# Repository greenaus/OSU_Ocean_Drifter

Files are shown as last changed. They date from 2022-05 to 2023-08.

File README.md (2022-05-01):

# OSU_Ocean_Drifter
The code repo for the HC 407 ocean drifter dev-kit

## ArudinoGPS.ino Dependencies:

Adafruit Unified Sensor  
Adafruit Circuit Playground  
Adafruit MAX31856 Library  
DHT sensor library  
Tiny GPS

## Current Arduino Pinout
### DHT Humidity Sensor:
plus  -> 5V

out   -> D2

minus -> GND

### GPS
VCC -> 5V  (Needs external source. Arudino can't provide enough power to run!)

RX  -> D3

TX  -> D4

GND -> GND

### Max31856 Thermocouple:
Vin -> 5V

GND -> GND

SCK -> D13

SDO -> D12

SDI -> D11

CS  -> D10

### SD Card (Tentative):
CS   -> D9

SCK  -> D13

MOSI -> D11

MISO -> D12

VCC  -> 5V

GND  -> GND

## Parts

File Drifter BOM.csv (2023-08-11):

Components | Description | Unit Price | Quantity | Address
LM3940IT-3.3/NOPB-ND | 3.3 V Regulator |  | 1
MAX6675ISA+TCT-ND | Thermocouple |  | 2
74VHC125MTCXCT-ND | Non-inv buffer |  | 1
490-GRM02YR60J104ME01LCT-ND | 0.1uF Cap |  | 3
490-10410-1-ND | 0.47uF Cap |  | 1
1276-2420-1-ND | 47uF Cap |  | 1
WM6357CT-ND | SD Card holder |  | 1
118-CR0805-FX-1300ELFCT-ND | 130 Ohm |  | 5
475-1410-1-ND | Green LED |  | 5
GY-NEO6MV2 NEO-6m | GPS |  | 1 | Amazon.com: HiLetgo GY-NEO6MV2 NEO-6M GPS Flight Controller Module 3V-5V with Super Strong Ceramic Antenna for Arduino EEPROM APM 2.5 : Electronics
LM2956 | Battery voltage regulator |  | 1
 | 2pin 2.54mm pitch screw terminal |  | 1 | https://www.amazon.com/Screw-Terminal-Connector-2-54mm-Universal/dp/B07QLXR1V9

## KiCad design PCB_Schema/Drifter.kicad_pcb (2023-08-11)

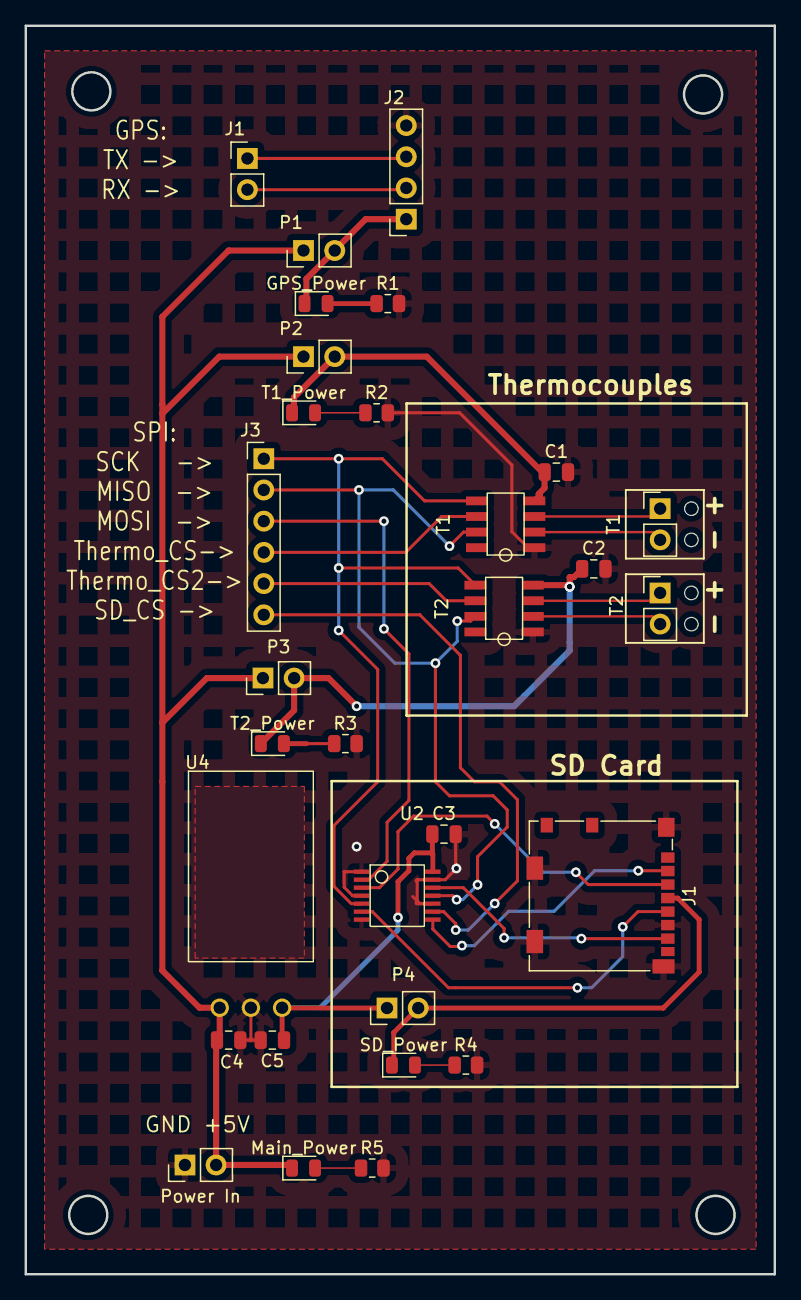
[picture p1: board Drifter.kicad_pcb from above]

Board: 2 copper layers, 61.0 x 101.6 mm, 30 parts (0 on the bottom side), 19 nets.

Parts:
C1, C2, C3, C4, C5: C_0805_2012Metric
GPS_Power: LED_0805_2012Metric
J1: microSD_HC_Molex_104031-0811
J1#2: PinHeader_1x02_P2.54mm_Vertical
J2: PinSocket_1x04_P2.54mm_Vertical
J3: PinHeader_1x06_P2.54mm_Vertical
Main_Power: LED_0805_2012Metric
P1, P2, P3, P4: PinHeader_1x02_P2.54mm_Vertical
Power In: PinHeader_1x02_P2.54mm_Vertical
R1, R2, R3, R4, R5: R_0805_2012Metric
SD_Power: LED_0805_2012Metric
T1, T2#2: PinHeader_1x02_P2.54mm_Vertical
T1#2, T2: Max6675
T1_Power, T2_Power: LED_0805_2012Metric
U2: 74VHC125
U4: LM3940

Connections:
+3.3V: C3.1, C5.1, J1.4, P4.1, P4.2, SD_Power.1, U2.14, U4.3
+5V: C1.1, C2.1, C4.1, GPS_Power.1, J2.1, Main_Power.1, P1.1, P1.2, P2.1, P2.2, P3.1, P3.2, Power In.2, T1#2.4, T1_Power.1, T2.4, T2_Power.1, U4.1
/CS_SD: J3.6, U2.9
/CS_Thermo: J3.4, T1#2.6
/MISO: J3.2, T1#2.7, T2.7, U2.11
/MOSI: J3.3, U2.2
/SCK: J3.1, T1#2.5, T2.5, U2.5
CD: J1.2, U2.8
CLK: J1.5, U2.6
CMD: J1.3, U2.3
CS_Thermo2: J3.5, T2.6
DAT0: J1.7, U2.12
GND: C1.2, C2.2, C3.2, C4.2, C5.2, J1.6, J1.11, J2.4, Power In.1, R1.2, R2.2, R3.2, R4.2, R5.2, T1#2.1, T2.1, U2.1, U2.4, U2.7, U2.10, U2.13, U4.2
RX: J1#2.2, J2.2
T2+: T2.3, T2#2.1
T2-: T2.2, T2#2.2
T+: T1.1, T1#2.3
T-: T1.2, T1#2.2
TX: J1#2.1, J2.3

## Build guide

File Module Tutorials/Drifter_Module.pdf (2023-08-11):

## Module Overview

Introduction

The Global Position System, or GPS, is an incredibly useful tool that has seen use in a variety of industries and applications. GPS is a part of the Global Navigation Satellite System (GNSS), and is used to provide geographical location and time to receivers. It has seen a variety of uses and is one of the primary sources of navigational data and positioning. GPS is reliant on a network of satellites orbiting the earth to provide an accurate approximation of a receivers location. A receiver needs a minimum of 4 satellites in order to accurately find its location. This is accomplished by each satellite sending a continuous message to each receiver containing its identification number, location in orbit, and time of transmission. Since the signals sent by the satellites travel at the speed of light, a distance can be calculated based off time of flight, and known speed of the message.

Hardware Overview

For this course, we are using a commonly used GPS module, the GY-NEO6MV2, which sees extensive use in battery operated and small form factor applications, such as drone racing. The NEO6MV2 is a standalone GPS receiver that provides location and time information over a standard Universal Asynchronous Receiver-Transmitter (UART), connection with a micro-controller, in this case our Arduino. This UART connection is typically made with 4 direct wired connections between the module and the micro-controller. Those four connections are VCC, RX, TX, and GND.

In our application, the module slots directly into the break out board, and only two connections are required to communicate with our controller, the RX and TX pins. RX is the ”receiver” channel for the module, and TX is the ”transmitter”. The RX pin on the module will connect with the TX pin on our Arduino, and the TX pin on our module will connect with the RX pin on the Arduino. A wiring diagram is provided below as well to illustrate this point.

As for the VCC and GND pins, these are the main source of power for the module. While normally it is possible to provide power for the module directly from the controller, in this case, we are providing power for the module through the break out board. VCC is a 5V input, while GND is the common ground.

1

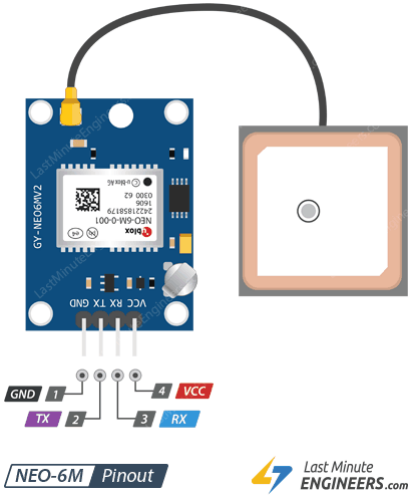
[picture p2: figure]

Figure 1: GPS Pinout

2

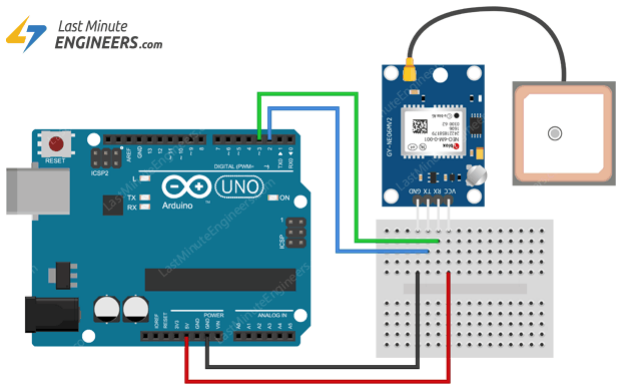
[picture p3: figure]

Figure 2: Wiring Diagram

## Module Pinout

## Wiring Guide

The figure above shows the wiring diagram used in this project. To connect the TX pin on the breakout board, to Pin 19 (RX1) on the Arduino Mega (Green Wire). RX on the breakout board, connects to Pin 18 (TX1) on the Arduino Mega (Blue Wire).

## Coding Guide

In order to use the GPS module after making these connections, we have to write some code for the Arduino to facilitate the communication. Since GPS uses a standardized communication protocol, there are numerous code libraries implemented for the Arduino to communicate with the module, and decipher the message coming from it. This module makes use of the TinyGPS++ library in the Arduino IDE. We use this library to open the serial communication ports on the Arduino, and decipher the NMEA sentences that come from the GPS unit. Below is the code you will need to get started.

Arduino

Libraries

3

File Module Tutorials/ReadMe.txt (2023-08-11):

This is the folder containing all of the tutorials for each module used in the Drifter project

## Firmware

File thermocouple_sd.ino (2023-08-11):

//libraries/files included
#include <MAX6675.h>
#include <SD.h>
#include <SPI.h>

//pin assignments
#define CS_PIN1 13
#define CS_PIN2 12
#define soPin = 50;
#define sckPin = 52;

//thermocouple initialization
MAX6675 tcouple1(CS_PIN1);
MAX6675 tcouple2(CS_PIN2);

File myFile; //file object

//data variables
int count = 0;
double temperature1 = 0;
double temperature2 = 0;
char myFileName[] = "test1.txt";
  
void setup() {
  //initialize serial
  Serial.begin(9600);

   //SD card initialization
  Serial.println("Initializing SD card...");
  if (!SD.begin(53)) {
    Serial.println("Initialization failed!");
    while(1);
  }
  Serial.println("Initialization done.");
  Serial.println();
  
 // if (SD.exists("data.txt")) SD.remove("data.txt"); //if there's already a file, delete it

//check the files name and create a new file
  for (int i = 1; i < 1000; i++) {
  char y = i+'0';
  myFileName[4] = y; // change the file name: test1.txt test2.txt.......
  
  if (SD.exists(myFileName)){ // if the file already exist
    continue;
    }
 
    Serial.println(myFileName); // Print the filename to which data is written before each run. 
    break;
  }
  
  //timer/counter1 initialization
  cli(); //stop interrupts
  TCCR1A = 0;
  TCCR1B = 0;
  TCNT1 = 0;
  OCR1A = 15624; // 1 Hz
  TCCR1B |= (1 << WGM12); //ctc mode
  TCCR1B |= (1 << CS12) | (1 << CS10); //prescaler
  TIMSK1 |= (1 << OCIE1A);
  sei(); //start interrupts
}

ISR(TIMER1_COMPA_vect) { //interrupt function to be called when timer reaches max
  count++; //increment count each second 
}

void loop() {

//run the part every 5 second.
if (count == 5) {
  
        //get thermocouples reading
        temperature1 = tcouple1.readTempC();
        temperature2 = tcouple2.readTempC();
        
        //print data to serial monitor
        Serial.print("Thermocouple 1 Temperature: ");
        Serial.println(temperature1);
        Serial.print("Thermocouple 2 Temperature: ");
        Serial.println(temperature2);
        Serial.println();
        
        //print data to sd card file
        myFile = SD.open(myFileName, FILE_WRITE);
        myFile.seek(EOF);

        myFile.print("Thermocouple 1 Temperature: ");
        myFile.println(temperature1);
        myFile.print("Thermocouple 2 Temperature: ");
        myFile.println(temperature2);

        myFile.println();
        
        myFile.close();

        count = 0; //reset count
      }
  if (count > 5) count = 0; //if count somehow exceeded max, reset it
}

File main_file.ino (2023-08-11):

#include <TinyGPS++.h>
#include <SD.h>
#include <SPI.h>
#include "max6675.h"

int sckPin = 52;
int soPin = 50;
int cs1Pin = 13;
int cs2Pin = 12;

MAX6675 thermocouple1(sckPin, cs1Pin, soPin);
MAX6675 thermocouple2(sckPin, cs2Pin, soPin);
TinyGPSPlus gps;
File myFile;

int count = 0;
double latitude = 0;
double longitude = 0;
double hours = 0;
double minutes = 0;
double seconds = 0;
float temp1_celsius = 0;
float temp2_celsius = 0;

void setup() {
  Serial.begin(9600);
  Serial1.begin(9600);

  //SD card initialization
  Serial.println("Initializing SD card...");
  if (!SD.begin(53)) {
    Serial.println("Initialization failed!");
    while(1);
  }
  Serial.println("Initialization done.");
  Serial.println();
  
  if (SD.exists("data.txt")) SD.remove("data.txt"); //if there's already a file, delete it

  //timer/counter1 initialization
  cli(); //stop interrupts
  TCCR1A = 0;
  TCCR1B = 0;
  TCNT1 = 0;
  OCR1A = 15624; // 1 Hz
  TCCR1B |= (1 << WGM12); //ctc mode
  TCCR1B |= (1 << CS12) | (1 << CS10); //prescaler
  TIMSK1 |= (1 << OCIE1A);
  sei(); //start interrupts
}

ISR(TIMER1_COMPA_vect) {
  count++; //increment count
}

void loop() {
  if (count == 5) {
    while (Serial1.available()) {
      gps.encode(Serial1.read());
      if (gps.location.isUpdated()) {
        latitude = gps.location.lat(), 6;
        longitude = gps.location.lng(), 6;
        hours = gps.time.hour();
        minutes = gps.time.minute();
        seconds = gps.time.second();
        temp1_celsius = thermocouple1.readCelsius();
        temp2_celsius = thermocouple2.readCelsius();

        Serial.print("Latitude: "); 
        Serial.print(latitude);
        Serial.print(", Longitude: "); 
        Serial.println(longitude);
        Serial.print("Hour: ");
        Serial.print(hours);
        Serial.print(", Minute: ");
        Serial.print(minutes);
        Serial.print(", Second: ");
        Serial.println(seconds);

        Serial.print("Thermocouple 1 Temperature: ");
        Serial.println(temp1_celsius);
        Serial.print("Thermocouple 2 Temperature: ");
        Serial.println(temp2_celsius);

        Serial.println();

        myFile = SD.open("data.txt", FILE_WRITE);
        myFile.seek(EOF);

        myFile.print("Latitude: "); 
        myFile.print(latitude);
        myFile.print(", Longitude: "); 
        myFile.println(longitude);
        myFile.print("Hour: ");
        myFile.print(hours);
        myFile.print(", Minute: ");
        myFile.print(minutes);
        myFile.print(", Second: ");
        myFile.println(seconds);

        myFile.print("Thermocouple 1 Temperature: ");
        myFile.println(temp1_celsius);
        myFile.print("Thermocouple 2 Temperature: ");
        myFile.println(temp2_celsius);

        myFile.println();
        
        myFile.close();

        count = 0;
      }
    }
  }
  if (count > 5) count = 0;
}

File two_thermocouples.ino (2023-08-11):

#include "max6675.h"

int sckPin = 52;
int soPin = 50;
int cs1Pin = 13;
int cs2Pin = 12;

MAX6675 thermocouple1(sckPin, cs1Pin, soPin);
MAX6675 thermocouple2(sckPin, cs2Pin, soPin);

void setup() {   
  Serial.begin(9600);
  delay(1000);
}

void loop() {
  float temperature1 = thermocouple1.readCelsius();
  float temperature2 = thermocouple2.readCelsius();
  Serial.print("Temperature 1: ");
  Serial.println(temperature1);
  Serial.print("Temperature 2: ");
  Serial.println(temperature2);
  delay(1000);
}

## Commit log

2022-04-05 Added Initial Arduino Code
2022-04-05 Updated ReadMe with Arduino Library dependencies
2022-04-12 Added Sensor Pinouts
2022-05-02 Updated KiCad PCB/Schema files
    [Drifter.kicad_pcb]
2022-07-21 Updated PCB
    [Drifter.kicad_pcb]
2022-09-11 Updated PCB and Schematic files
2022-09-11 Basic Project BOM
    [Drifter BOM.csv]
2022-09-13 Uploaded GPS tutorial prototype
2022-09-19 Update Drifter BOM.csv
    [Drifter BOM.csv]
